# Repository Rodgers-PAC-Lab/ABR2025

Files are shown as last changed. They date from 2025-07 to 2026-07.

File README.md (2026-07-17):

# ABR2025

## Introduction

This repository contains code to implement the ABR measuring system described
in Gargiullo et al, as well as the analysis scripts needed to replicate the 
figures in that paper.
Preprint: https://www.biorxiv.org/content/10.64898/2025.12.17.694771v1

The repository is structured as follows:
- `./` - The toplevel directory, containing this README file
- `./designs` - Design files, bill of materials, and other information about 
physically building the system.
- `./src` - source code for analysis and GUI. Import like `import opensabr`
- `./src/gui` - A Python module for running the graphical user interface (GUI) 
to take ABR data. It can be imported like `import opensabr.gui`. This code is 
run on a desktop PC connected to the ABR measuring system hardware.
- `./scripts` - A folder of demo scripts that generate the figures in the
paper, using data that we collected and have shared on Zenodo. These scripts 
are meant to be run one at a time, not imported and called by other scripts. 

## Requirements

We used Python 3.11. Newer versions may also work but we did not test them.

requirements-lock.txt includes the exact versions we used

For the analysis scripts (but not the GUI), the following repository is 
required. It should be on your PYTHONPATH so that it can be imported using
the syntax `import my`.
- `git clone git@github.com:Rodgers-PAC-Lab/my.git`

TODO: only my.plot is needed, bring minimal into this repo

## Instructions

To build the hardware, refer to the file `./designs/README`. 

To run the GUI and measure ABR, refer to the file `./gui/README`.

To run the analysis scripts and regenerate the figures included in the paper,
refer to the file `./scripts/README`.

## Overall installation instructions
These instructions walk you through the installation of OpenSABR, our fork
of ABRA, and our fork of ABRpresto in three different conda environments.
If you only want to run OpenSABR, you can skip the other two environments --
they are only used to provide a point of comparison in the paper. 

We clone repositories that are installed using a method like `pip install`
into a directory called `~/dev/installed`. We clone repositories that are 
not installable, but need to be imported, into a directory called `~/dev`.
ABRA is the only one that must be cloned into `~/dev`.
This is because it can cause errors to mix these two kinds of repositories.
`~/dev` must be on the PYTHONPATH for this to work. 

For ABRA, we recommend the CPU packages, there is no need for GPU.

The three conda environments share data written to disk in the parquet format.

## Installing OpenSABR
# Clone repo
cd ~/installed
git clone git@github.com:Rodgers-PAC-Lab/OpenSABR
cd OpenSABR

# --- Install: pick ONE of Option A or Option B ---

# Option A: Typical install (no version pins)
conda create -n opensabr -c conda-forge python=3.11 pip ipython
conda activate opensabr
conda install -c conda-forge numpy scipy pandas matplotlib tqdm pyqt pyqtgraph pyserial pyarrow seaborn
pip install -e . --no-deps

# Option B: Reproducible install from lock (linux-64 only)
conda create -n opensabr --file opensabr-conda-lock.txt
conda activate opensabr
pip install -e . --no-deps

## Installing ABRpresto
# Clone repo
cd ~/installed 
git clone git@github.com:Rodgers-PAC-Lab/ABRpresto # our fork
cd ABRpresto
git checkout dev # our branch with fixes

# --- Install: pick ONE of Option A or Option B ---

# Option A: Typical install (no version pins)
conda create -n abrpresto -c conda-forge python=3.11 ipython pip
conda activate abrpresto
conda install -c conda-forge numpy scipy pandas matplotlib setuptools_scm pyarrow tqdm
pip install -e . --no-deps

# Option B: Reproducible install from lock (linux-64 only)
conda create -n abrpresto --file abrpresto-conda-lock.txt
conda activate abrpresto
pip install -e . --no-deps

## Installing ABRA
# Clone repo (must be under ~/dev or some location on PYTHONPATH)
cd ~/dev
git clone git@github.com:Rodgers-PAC-Lab/abranalysis # our fork
cd abranalysis
git checkout dev # our branch with fixes

# --- Install: pick ONE of Option A or Option B ---
# ABRA cannot be pip-installed; it is imported via PYTHONPATH in both options.

# Option A: Typical install (no version pins)
conda create -n abra -c conda-forge python=3.11 ipython pip
conda activate abra
conda install -c conda-forge numpy scipy pandas scikit-learn pytorch=*=cpu* keras tensorflow streamlit easydict "altair<5" pyarrow matplotlib tqdm
conda env config vars set PYTHONPATH=$HOME/dev
conda deactivate && conda activate abra   # reload so PYTHONPATH takes effect

# Option B: Reproducible install from lock (linux-64 only)
conda create -n abra --file abra-conda-lock.txt
conda activate abra
conda env config vars set PYTHONPATH=$HOME/dev
conda deactivate && conda activate abra   # reload so PYTHONPATH takes effect

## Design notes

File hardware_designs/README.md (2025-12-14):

# ABR2025 - hardware designs

## Introduction 

This folder contains the designs needed to build the hardware for the 
ABR measuring system described in Gargiullo 2025.

It contains the following subfolders:
- bill_of_materials.xlsx: Bill of Materials for all required parts
- interface_pcb/: PCB design files for the "interface PCB" that houses the
Teensy and connects to the other boards
- teensy/: Files for the code that runs on the Teensy

### Bill of Materials

This is an Excel file of all required components. You will also need standard
electronics equipment for soldering, etc.

### Interface PCB

This PCB was designed in Eagle. The original design files are located in the
`eagle` subdirectory and can be opened in the Eagle software. You only need to 
do this if you want to edit the PCB.

If you just want to print the PCB, use the files in the `gerbers` subdirectory.
These are the standard manufacturing format that all PCB printing companies use.
We used OSH Park to print the PCB.

After you receive the PCB, you will need to populate a few components. Details
are available in the "Supplemental Material", which also explains how to 
physically assemble all components.

### Teensy files

This is the software that runs on the Teensy. The software controls the 
ADS1299, and it also interfaces with the desktop computer running the GUI
(see `../gui/README`). Flash the files included here on the Teensy.

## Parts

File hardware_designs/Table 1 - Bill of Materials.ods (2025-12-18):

Item # | Component name | Manufacturer | Part number | Vendor | Quantity | Price per unit | Total price | Notes | Link
1 | ADS1299 Performance Demonstration Kit | TI | ADS1299EEGFE-PDK | Ti | 1 | 199 | 199 | Available on Digikey for $238. Added to the DigiKey BOM but don't recoomend buying through them due to markup. | https://www.ti.com/tool/ADS1299EEGFE-PDK
2 | Teensy 4.0 | Sparkfun | 1568-15583-ND | DigiKey | 1 | 23.8 | 23.8 |  | https://www.digikey.com/en/products/detail/sparkfun-electronics/15583/10384551
3 | Mini banana plug solderless stacking | Pomona | 2945 | DigiKey | 9 | 6.09 | 54.81 | 2 each * 4 channels (3 neural channels + audio channel) + 1 for ground. On DigiKey list version of this BOM I added red and black versions. | https://www.digikey.com/en/products/base-product/pomona-electronics/501/2945/525904
4 | Mini banana jack (turret style) | Pomona | 2142-2 | DigiKey | 9 | 2.9 | 26.1 | On DigiKey list version of this BOM I added red and black versions. | https://www.digikey.com/en/products/base-product/pomona-electronics/501/2142/427743
5 | Mini grabber solder 0.090" | Pomona | 3925 | DigiKey | 6 | 2.54 | 15.24 | 3 for electrodes, 1 for ground electrode, 2 for speaker power. On DigiKey list version of this BOM I added grabbers of several different colors | https://www.digikey.com/en/products/base-product/pomona-electronics/501/3925/525917
6 | USB-B to USB-A adapter | Switchcraft Inc | SC1837-ND | DigiKey | 1 | 22.26 | 22.26 | USB form factor not important, just needs a panel mount feed-through | https://www.digikey.com/en/products/detail/switchcraft-inc/EHUSBBABX/1832371
7 | 3/4" #4-40 Aluminum hex standoff | Keystone Electronics | 36-8403-ND | DigiKey | 4 | 0.71 | 2.84 | Supports interface PCB, 2x stacked on 2 legs | https://www.digikey.com/en/products/detail/keystone-electronics/8403/255370
8 | 7/8" #4-40 Aluminum hex standoff | Keystone Electronics | 36-8404-ND | DigiKey | 2 | 1 | 2 | Supports ADS1299 daughterboard | https://www.digikey.com/en/products/detail/keystone-electronics/8404/255371
9 | 3/8" #4-40 nylon hex standoff F-F | Keystone Electronics | 36-1902B-ND | DigiKey | 4 | 0.62 | 2.48 | Glued to bottom of MMB0 | https://www.digikey.com/en/products/detail/keystone-electronics/1902B/61866
10 | Hammond 1598GBK | Hammond | 1598 GBK | DigiKey | 1 | 27.86 | 27.86 | Device enclosure | https://www.digikey.com/en/products/detail/hammond-manufacturing/1598GBK/131059
11 | DC-to-DC converter | Recom power | R-78E5.0-0.5 | DigiKey | 1 | 3.3 | 3.3 | Step-down 9V to Teensy | https://www.digikey.com/en/products/detail/recom-power/R-78E5-0-0-5/2834904
12 | 3-conductor cable (24 AWG) | Tensility | 30-01424 | DigiKey | 1 | 5.17 | 5.17 | Priced per meter | https://www.digikey.com/en/products/detail/tensility-international-corp/30-01424/13151644
13 | Molex KK254 2-pin PCB header | Molex | 900-002222021-ND | DigiKey | 1 | 0.16 | 0.16 | Power connector X1 on interface PCB | https://www.digikey.com/en/products/detail/molex/0022232021/26667
14 | Molex KK254 2-pos receptacle | Molex | 900-0022013027-ND | DigiKey | 1 | 0.1 | 0.1 | Power cable connector for MMB0 power to interface PCB | https://www.digikey.com/en/products/detail/molex/0022013027/26431
15 | Pre-crimped 12" A2016 (KK254 series) wires | Molex | 0008500113-12-B2-D-ND | DigiKey | 2 | 0.85 | 1.7 | Fits into KK254 power cable receptacle | https://www.digikey.com/en/products/detail/molex/0008500113-12-B2-D/5991033
16 | 10 µH Inductor | Taiyo Yuden | 587-1625-1-ND | DigiKey | 2 | 0.18 | 0.36 |  | https://www.digikey.com/en/products/detail/taiyo-yuden/CBC3225T100MR/958009
17 | 220 µF capacitor | Panasonic | PCE3839CT-ND | DigiKey | 1 | 0.85 | 0.85 |  | https://www.digikey.com/en/products/detail/panasonic-electronic-components/EEE-FK1V221P/766007
18 | 100 µF capacitor | Nichicon | 493-3937-1-ND | DigiKey | 1 | 0.61 | 0.61 |  | https://www.digikey.com/en/products/detail/nichicon/UCL1E101MCL1GS/2300286
19 | 1 µF capacitor | Samsung | 1276-1066-1-ND | DigiKey | 1 | 0.08 | 0.08 |  | https://www.digikey.com/en/products/detail/samsung-electro-mechanics/CL21B105KAFNNNE/3886724
20 | 0.1 µF (100 nF) capacitor | Samsung | 1276-1099-1-ND | DigiKey | 3 | 0.08 | 0.24 |  | https://www.digikey.com/en/products/detail/samsung-electro-mechanics/CL21B104KACNNNC/3886757
21 | Needle electrodes | Rochestor Horizon | NS-S86015-R1-10 | Lifesync | 4 per recording |  |  | 4 electrodes per recording (L, R, V, GND) | https://lifesync.com/products/horizon-multilead-ribbon-subdermal-needle-electrodes-variants
22 | Speaker- horn tweeter | Fostex | FT17H | Fostex | 2 | NA | NA |  | Discontinued
23 | USB serial UART converter | Acroname | S27-USB-SERIAL | Acroname | 1 | 12.5 | 12.5 | Optional | https://acroname.com/store/s27-usb-serial#assets

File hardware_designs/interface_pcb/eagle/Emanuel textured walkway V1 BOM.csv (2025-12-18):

Partlist exported from C:/Users/Bill/Dropbox/EAGLE/projects/
Alan Emanuel textured walkway/Emanuel textured walkway V1.sch at 4/9/2025 10:39 AM
Qty | Value | Device | Parts
3 | 1uF | C-USC0805 | C5, C6, C7
1 | 3.3 | TP-040-100 | 3.3
3 | 10uH | L-USL1812 | L1, L2, L3
1 | 22-23-2021 | 22-23-2021 | X1
1 | 74LS14D | 74LS14D | IC10
2 | 78E-5V | RECOM-R-78E | IC8, IC9
1 | 78E-12V | RECOM-R-78E | IC7
3 | 100/35 | CPOL-US140CLH-0810 | C2, C3, C4
3 | 100nF | C-USC0805 | C8, C9, C10
1 | 330/35 | CPOL-US140CLH-1010 | C1
6 | BTS3118N | BTS3118N | IC1, IC2, IC3, IC4, IC5, IC6
1 | EXTRA | ML16 | SV3
1 | I/O-1 | ML16 | SV2
1 | STEPPER | ML16 | SV1
1 | TEENSY_4.0_WITH_24-33 | TEENSY_4.0_WITH_24-33 | U$1
38 | TP-040-100 | TP-040-100 | +5B, 6, 7, 22, 23, 24, 25, 26, 27, 28, 29, 30, 31, 32, 33, E9, E10, E11, E12, E13, E14, E15, E16, EI1, EI2, EI3, EO1, EO2, EO3, MISO, MOSI, RX1, SCK, TX1, VI3, VS1, VS2, VS3
1 | TRCV-175-LARGE | TRCV-175-LARGE | J1

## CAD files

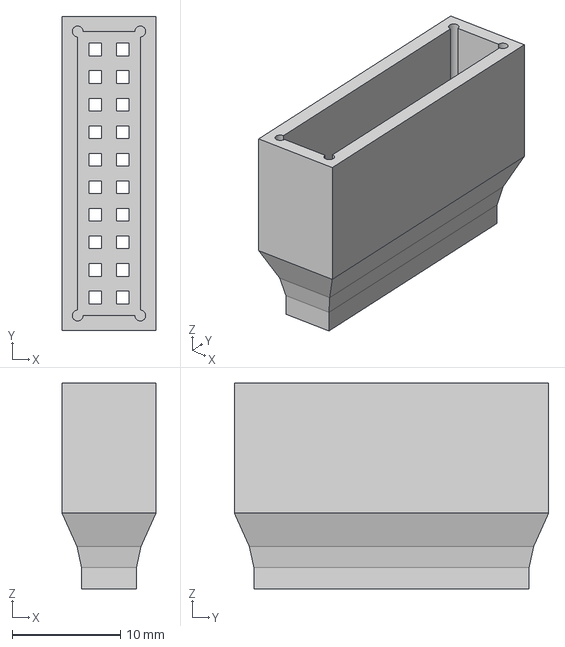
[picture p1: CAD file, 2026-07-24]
hardware_designs/3D_print_designs/2x10 male pin header spacer.step
8.68 x 29.0 x 19.0 mm

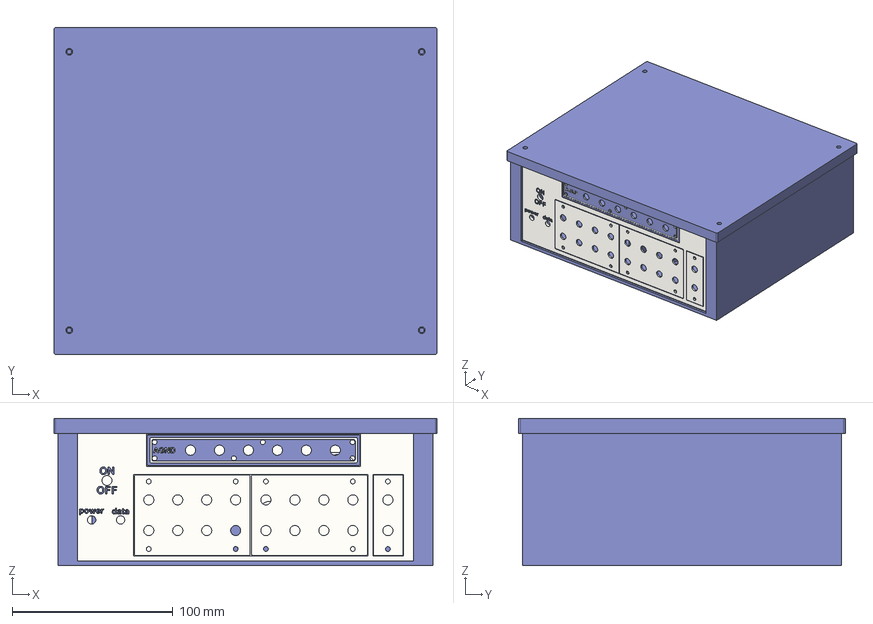
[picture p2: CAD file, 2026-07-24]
hardware_designs/3D_print_designs/Compact ABR enclosure.step
238.0 x 203.0 x 91.5 mm
face plate
Back plate
Lid

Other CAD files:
hardware_designs/3D_print_designs/2x10 male pin header spacer.3mf
hardware_designs/3D_print_designs/2x10 male pin header spacer.f3d
hardware_designs/3D_print_designs/Compact ABR enclosure.3mf
hardware_designs/3D_print_designs/Compact ABR enclosure.f3z

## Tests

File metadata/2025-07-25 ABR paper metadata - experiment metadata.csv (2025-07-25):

date | experimenter | mouse
2025-04-30 | rowan | Pearl_189
2025-05-02 | rowan | Cacti_1
2025-05-06 | rowan | Cat_226
2025-05-06 | rowan | Cat_227
2025-05-09 | rowan | Cat_226
2025-05-09 | rowan | Cat_227
2025-05-12 | rowan | Cat_226
2025-05-12 | rowan | Cat_227
2025-05-14 | rowan | Cat_226
2025-05-14 | rowan | Cat_227
2025-05-15 | rowan | Cat_228
2025-05-15 | rowan | Cat_229
2025-05-20 | rowan | Cat_228
2025-05-20 | rowan | Cat_229
2025-05-24 | rowan | Cat_228
2025-05-24 | rowan | Cat_229
2025-05-27 | rowan | Cat_228
2025-05-27 | rowan | Cat_229
2025-06-02 | rowan | Cacti_223
2025-06-02 | rowan | Cacti_225
2025-06-06 | rowan | Cacti_223
2025-06-06 | rowan | Cacti_224

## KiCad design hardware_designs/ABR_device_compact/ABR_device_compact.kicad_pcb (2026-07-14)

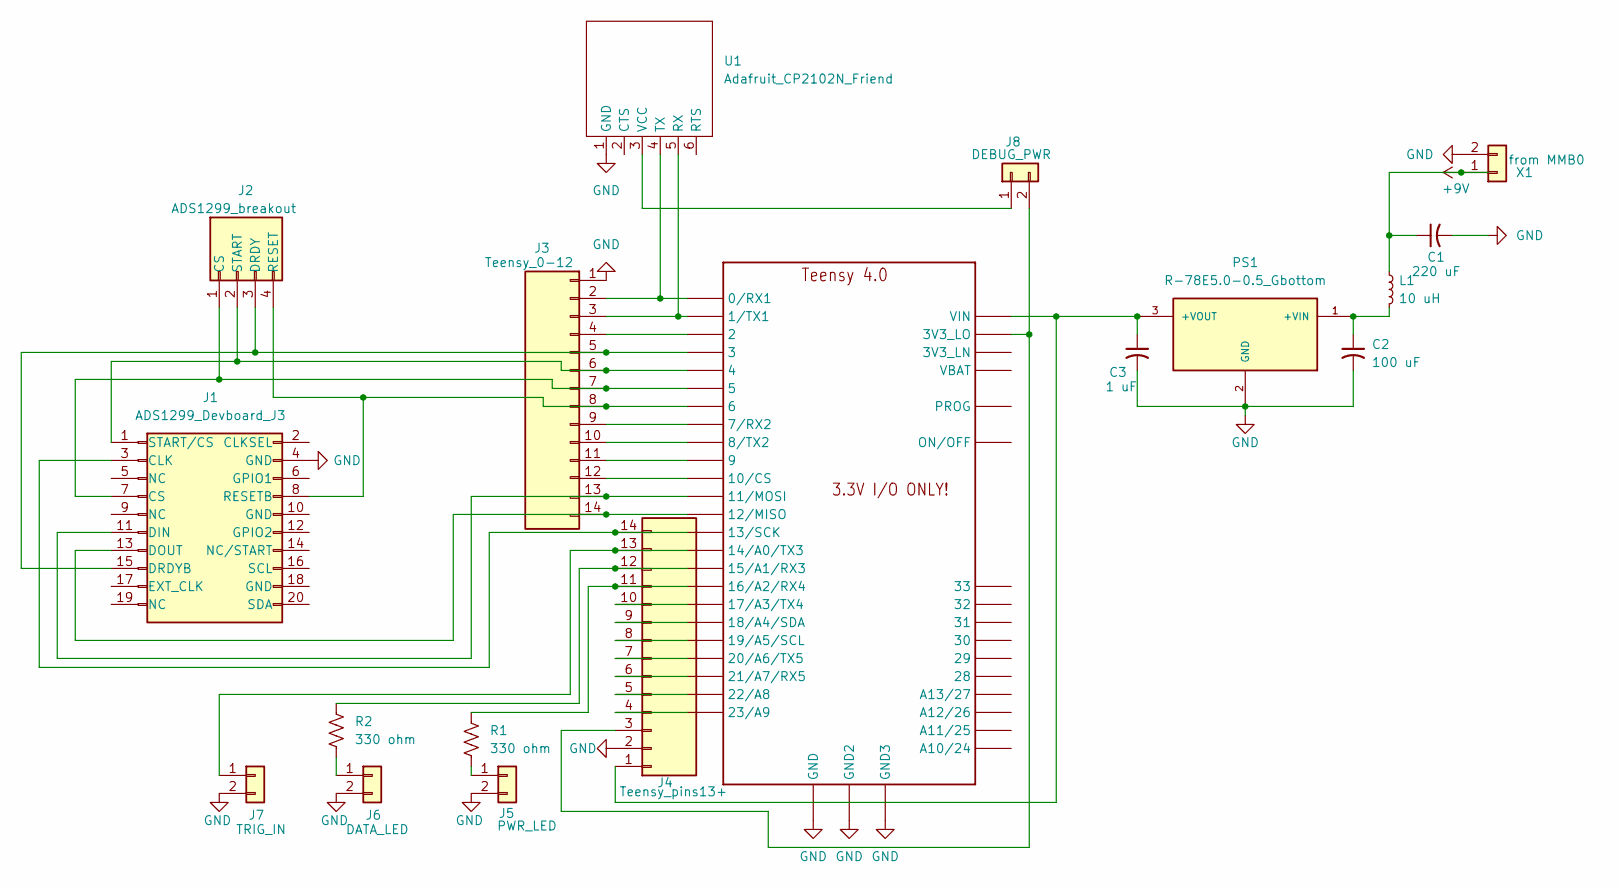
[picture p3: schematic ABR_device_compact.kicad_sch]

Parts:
1: TEENSY_4.0_WITH_24-33
C1: 220 uF; CP_Radial_D10.0mm_P5.00mm
C2: 100 uF; CP_Radial_D8.0mm_P3.80mm
C3: 1 uF; CP_Radial_D7.5mm_P2.50mm
J1: ADS1299_Devboard_J3; IDC-Header_2x10_P2.54mm_Vertical
J2: ADS1299_breakout; PinSocket_1x04_P2.54mm_Vertical
J3: Teensy_0-12; PinHeader_1x14_P2.54mm_Vertical
J4: Teensy_pins13+; PinHeader_1x14_P2.54mm_Vertical
J5: PWR_LED; PinHeader_1x02_P2.54mm_Vertical
J6: DATA_LED; PinHeader_1x02_P2.54mm_Vertical
J7: TRIG_IN; PinHeader_1x02_P2.54mm_Vertical
J8: DEBUG_PWR; PinHeader_1x02_P2.54mm_Vertical
L1: 10 uH; L_Axial_L9.5mm_D4.0mm_P15.24mm_Horizontal_Fastron_SMCC
PS1: R-78E5.0-0.5_Gbottom; CONV_R-78E5.0-0.5; PARTREV v4
R1, R2: 330 ohm; R_Axial_DIN0207_L6.3mm_D2.5mm_P10.16mm_Horizontal
U1: Adafruit_CP2102N_Friend
X1: from MMB0; JST_XH_B2B-XH-A_1x02_P2.50mm_Vertical

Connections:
+9V: C1.1, L1.1, X1.1
GND: 1.GND, 1.GND2, 1.GND3, C1.2, C2.2, C3.2, J1.4 (GND), J3.1, J4.2, J5.2, J6.2, J7.2, PS1.2 (GND), U1.1 (GND), X1.2
unnamed: 1.0/RX (0/RX1), J3.2, U1.4 (TX)
unnamed: 1.1/TX (1/TX1), J3.3, U1.5 (RX)
unnamed: 1.7 (7/RX2), J3.9
unnamed: 1.8 (8/TX2), J3.10
unnamed: 1.14/A0 (14/A0/TX3), J4.13, J7.1
unnamed: 1.15/A1 (15/A1/RX3), J4.12, R2.1
unnamed: 1.16/A2 (16/A2/RX4), J4.11, R1.1
unnamed: 1.17/A3 (17/A3/TX4), J4.10
unnamed: 1.20/A6 (20/A6/TX5), J4.7
unnamed: 1.21/A7 (21/A7/RX5), J4.6
unnamed: 1.13/SCK, J1.3 (CLK), J4.14
unnamed: 1.5, J1.7 (CS), J2.1 (CS), J3.7
unnamed: 1.11/MOSI, J1.11 (DIN), J3.13
unnamed: 1.12/MISO, J1.13 (DOUT), J3.14
unnamed: 1.3, J1.15 (DRDYB), J2.3 (DRDY), J3.5
unnamed: 1.6, J1.8 (RESETB), J2.4 (RESET), J3.8
unnamed: 1.4, J1.1 (START/CS), J2.2 (START), J3.6
unnamed: 1.2, J3.4
unnamed: 1.9, J3.11
unnamed: 1.10/CS, J3.12
unnamed: 1.VIN, C3.1, J4.1, PS1.3 (+VOUT)
unnamed: 1.3V3_LO, J4.3, J8.2
unnamed: 1.23/A9, J4.4
unnamed: 1.22/A8, J4.5
unnamed: 1.19/A5/SCL, J4.8
unnamed: 1.18/A4/SDA, J4.9
unnamed: J5.1, R1.2
unnamed: J6.1, R2.2
unnamed: J8.1, U1.3 (VCC)
unnamed: C2.1, L1.2, PS1.1 (+VIN)

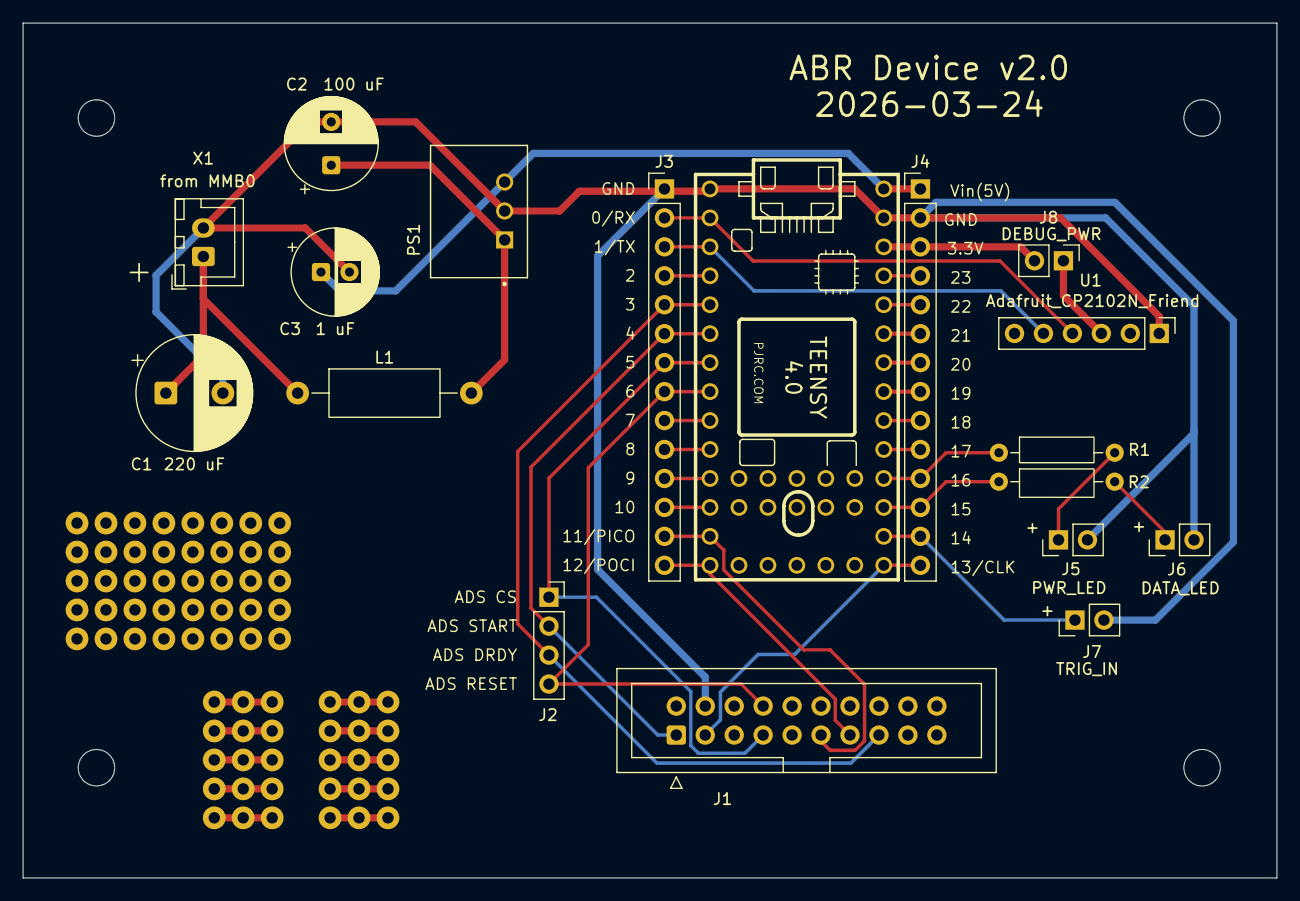
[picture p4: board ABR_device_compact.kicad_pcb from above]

Board: 2 copper layers, 110.0 x 75.0 mm, 87 parts (0 on the bottom side), 32 nets.

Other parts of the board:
2, 3, 4, 5, 6, 7, 8, 9, 9#2, 10, 11, 12, 13, 14, 15, 16, 17, 17#2, 18, 19, 20, 21, 22, 23, 24, 25, 25#2, 26, 27, 28, 29, 30, 31, 32, 33, 34, 35, 36, 37, 38, 39, 40, 41, 41#2, 42, 43, 44, 45, 46, 47, 48, 49, 57, 58, 59, 60, 61, 62, 63, 64, 65, 66, 67, 68, 69, 70, 71, 72, 73: (no value)

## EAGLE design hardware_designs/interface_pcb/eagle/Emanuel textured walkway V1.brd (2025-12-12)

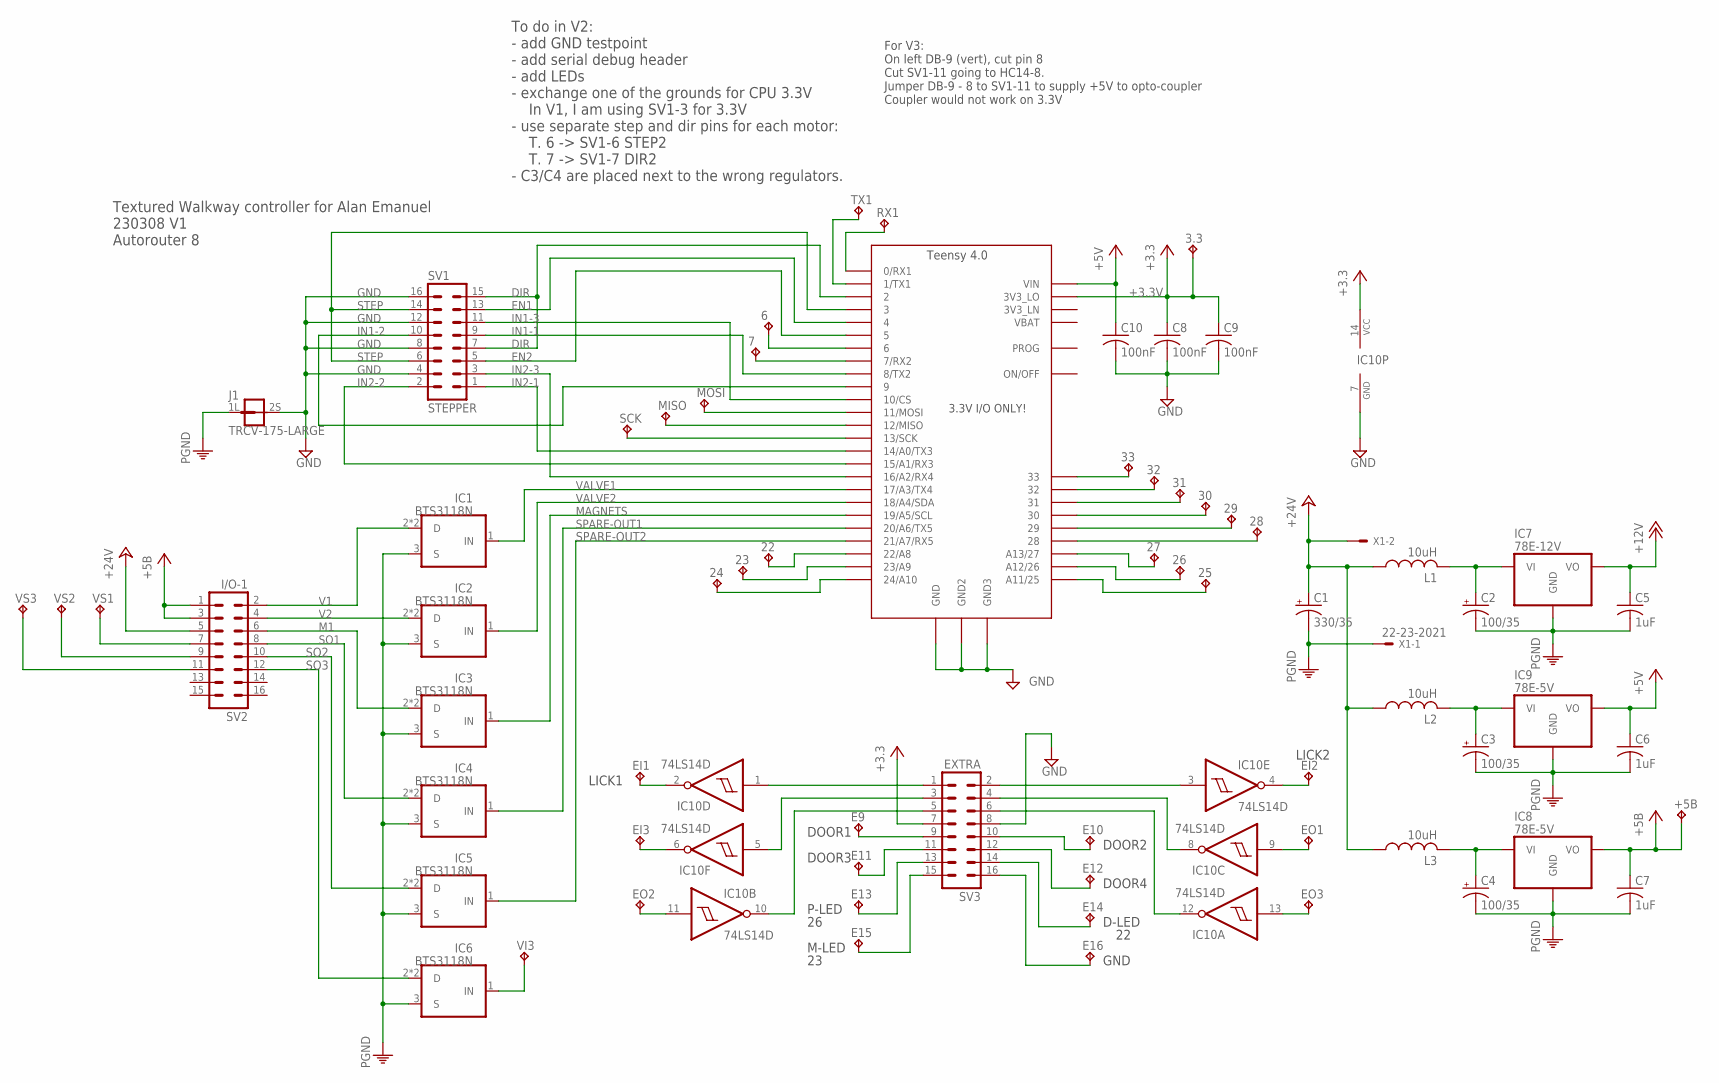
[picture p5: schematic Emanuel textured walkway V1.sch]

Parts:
3.3: 3.3; P1-040-100
6, 7, 22, 23, 24, 25, 26, 27, 28, 29, 30, 31, 32, 33: TP-040-100; P1-040-100
+5B: TP-040-100; P1-040-100
C1: 330/35; 140CLH-1010
C2, C3, C4: 100/35; 140CLH-0810
C5, C6, C7: 1uF; C0805
C8, C9, C10: 100nF; C0805
E9, E10, E11, E12, E13, E14, E15, E16: TP-040-100; P1-040-100
EI1, EI2, EI3: TP-040-100; P1-040-100
EO1, EO2, EO3: TP-040-100; P1-040-100
IC1, IC2, IC3, IC4, IC5, IC6: BTS3118N; SOT223
IC7: 78E-12V; RECOM-R-78E
IC8, IC9: 78E-5V; RECOM-R-78E
IC10: 74LS14D; SO14
J1: TRCV-175-LARGE; JUMPER-TRACE-CONVERT-LARGER-PADS-175
L1, L2, L3: 10uH; L1812
MISO: TP-040-100; P1-040-100
MOSI: TP-040-100; P1-040-100
RX1: TP-040-100; P1-040-100
SCK: TP-040-100; P1-040-100
SV1: STEPPER; ML16
SV2: I/O-1; ML16
SV3: EXTRA; ML16
TX1: TP-040-100; P1-040-100
U$1: TEENSY_4.0_WITH_24-33
VI3: TP-040-100; P1-040-100
VS1, VS2, VS3: TP-040-100; P1-040-100
X1: 22-23-2021

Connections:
+3.3V: 3.3.P$1, C8.1, C9.1, IC10.14 (VCC), SV3.7, U$1.3V3_LO
+5B: +5B.P$1, C7.1, IC8.3 (VO), SV2.1, SV2.3
+5V: C6.1, C10.1, IC9.3 (VO), U$1.VIN
+12V: C5.1, IC7.3 (VO)
+24V: C1.+, L1.1, L2.1, L3.1, SV2.5, X1.2
DIR: SV1.7, SV1.15, U$1.2
EN1: SV1.13, U$1.4
EN2: SV1.5, U$1.5
GND: C8.2, C9.2, C10.2, IC10.7 (GND), J1.2S (2), SV1.4, SV1.8, SV1.12, SV1.16, SV3.8, U$1.GND, U$1.GND2, U$1.GND3
IN1-1: SV1.9, U$1.8 (8/TX2)
IN1-2: SV1.10, U$1.9
IN1-3: SV1.11, U$1.10/CS
IN2-1: SV1.1, U$1.14/A0 (14/A0/TX3)
IN2-2: SV1.2, U$1.15/A1 (15/A1/RX3)
IN2-3: SV1.3, U$1.16/A2 (16/A2/RX4)
M1: IC3.2 (D), IC3.4 (D), SV2.6
MAGNETS: IC3.1 (IN), U$1.19/A5/SCL
unnamed: C2.+, IC7.1 (VI), L1.2
unnamed: C4.+, IC8.1 (VI), L3.2
unnamed: SV2.9, VS2.P$1
unnamed: SV2.11, VS3.P$1
unnamed: C3.+, IC9.1 (VI), L2.2
unnamed: IC6.1 (IN), VI3.P$1
unnamed: MOSI.P$1, U$1.11/MOSI
unnamed: MISO.P$1, U$1.12/MISO
unnamed: SV2.7, VS1.P$1
unnamed: SCK.P$1, U$1.13/SCK
unnamed: 22.P$1, U$1.22/A8
unnamed: 23.P$1, U$1.23/A9
unnamed: 24.P$1, U$1.24 (24/A10)
unnamed: 33.P$1, U$1.33
unnamed: 32.P$1, U$1.32
unnamed: 31.P$1, U$1.31
unnamed: 30.P$1, U$1.30
unnamed: 29.P$1, U$1.29
unnamed: 28.P$1, U$1.28
unnamed: 27.P$1, U$1.27 (A13/27)
unnamed: 26.P$1, U$1.26 (A12/26)
unnamed: 25.P$1, U$1.25 (A11/25)
unnamed: RX1.P$1, U$1.0/RX (0/RX1)
unnamed: TX1.P$1, U$1.1/TX (1/TX1)
unnamed: 6.P$1, U$1.6
unnamed: 7.P$1, U$1.7 (7/RX2)
unnamed: IC10.1 (I), SV3.1
unnamed: IC10.3 (I), SV3.2
unnamed: IC10.5 (I), SV3.3
unnamed: IC10.8 (O), SV3.4
unnamed: IC10.10 (O), SV3.5
unnamed: IC10.12 (O), SV3.6
unnamed: E9.P$1, SV3.9
unnamed: E11.P$1, SV3.11
unnamed: E13.P$1, SV3.13
unnamed: E15.P$1, SV3.15
unnamed: E10.P$1, SV3.10
unnamed: E12.P$1, SV3.12
unnamed: E14.P$1, SV3.14
unnamed: E16.P$1, SV3.16
unnamed: EI1.P$1, IC10.2 (O)
unnamed: EI3.P$1, IC10.6 (O)
unnamed: EI2.P$1, IC10.4 (O)
unnamed: EO3.P$1, IC10.13 (I)
unnamed: EO1.P$1, IC10.9 (I)
unnamed: EO2.P$1, IC10.11 (I)
PGND: C1.-, C2.-, C3.-, C4.-, C5.2, C6.2, C7.2, IC1.3 (S), IC2.3 (S), IC3.3 (S), IC4.3 (S), IC5.3 (S), IC6.3 (S), IC7.2 (GND), IC8.2 (GND), IC9.2 (GND), J1.1L (1), X1.1
SO1: IC4.2 (D), IC4.4 (D), SV2.8
SO2: IC5.2 (D), IC5.4 (D), SV2.10
SO3: IC6.2 (D), IC6.4 (D), SV2.12
SPARE-OUT1: IC4.1 (IN), U$1.20/A6 (20/A6/TX5)
SPARE-OUT2: IC5.1 (IN), U$1.21/A7 (21/A7/RX5)
STEP: SV1.6, SV1.14, U$1.3
V1: IC1.2 (D), IC1.4 (D), SV2.2
V2: IC2.2 (D), IC2.4 (D), SV2.4
VALVE1: IC1.1 (IN), U$1.17/A3 (17/A3/TX4)
VALVE2: IC2.1 (IN), U$1.18/A4/SDA

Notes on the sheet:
Textured Walkway controller for Alan Emanuel 230308 V1 Autorouter 8
To do in V2: - add GND testpoint - add serial debug header - add LEDs - exchange one of the grounds for CPU 3.3V In V1, I am using SV1-3 for 3.3V - use separate step and dir pins for each motor: T. 6 -> SV1-6 STEP2 T. 7 -> SV1-7 DIR2 - C3/C4 are placed next to the wrong regulators.
LICK1
LICK2
DOOR1
DOOR3
DOOR2
DOOR4
P-LED
M-LED
D-LED
GND
For V3: On left DB-9 (vert), cut pin 8 Cut SV1-11 going to HC14-8. Jumper DB-9 - 8 to SV1-11 to supply +5V to opto-coupler Coupler would not work on 3.3V

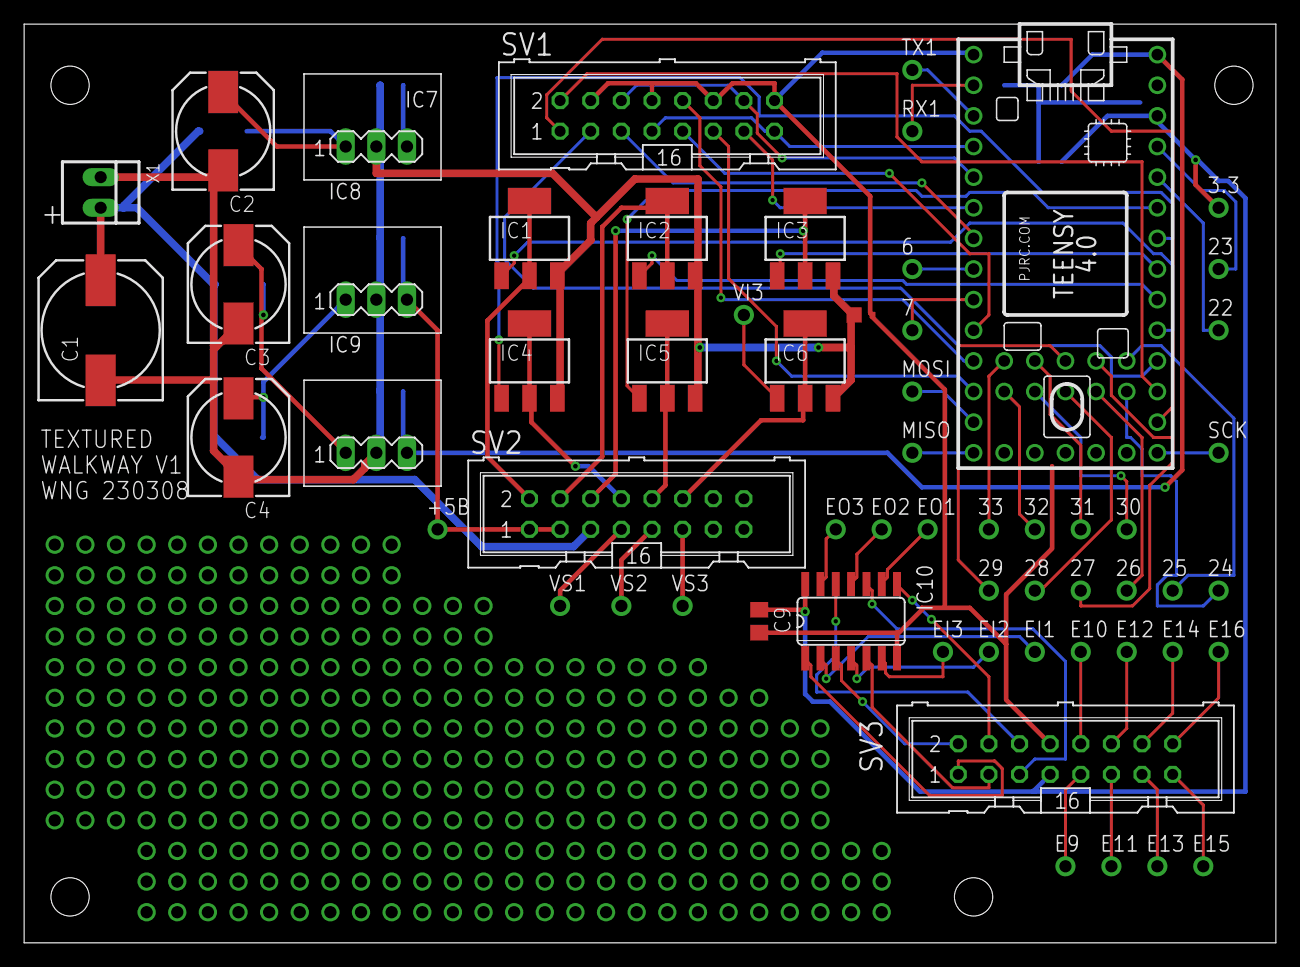
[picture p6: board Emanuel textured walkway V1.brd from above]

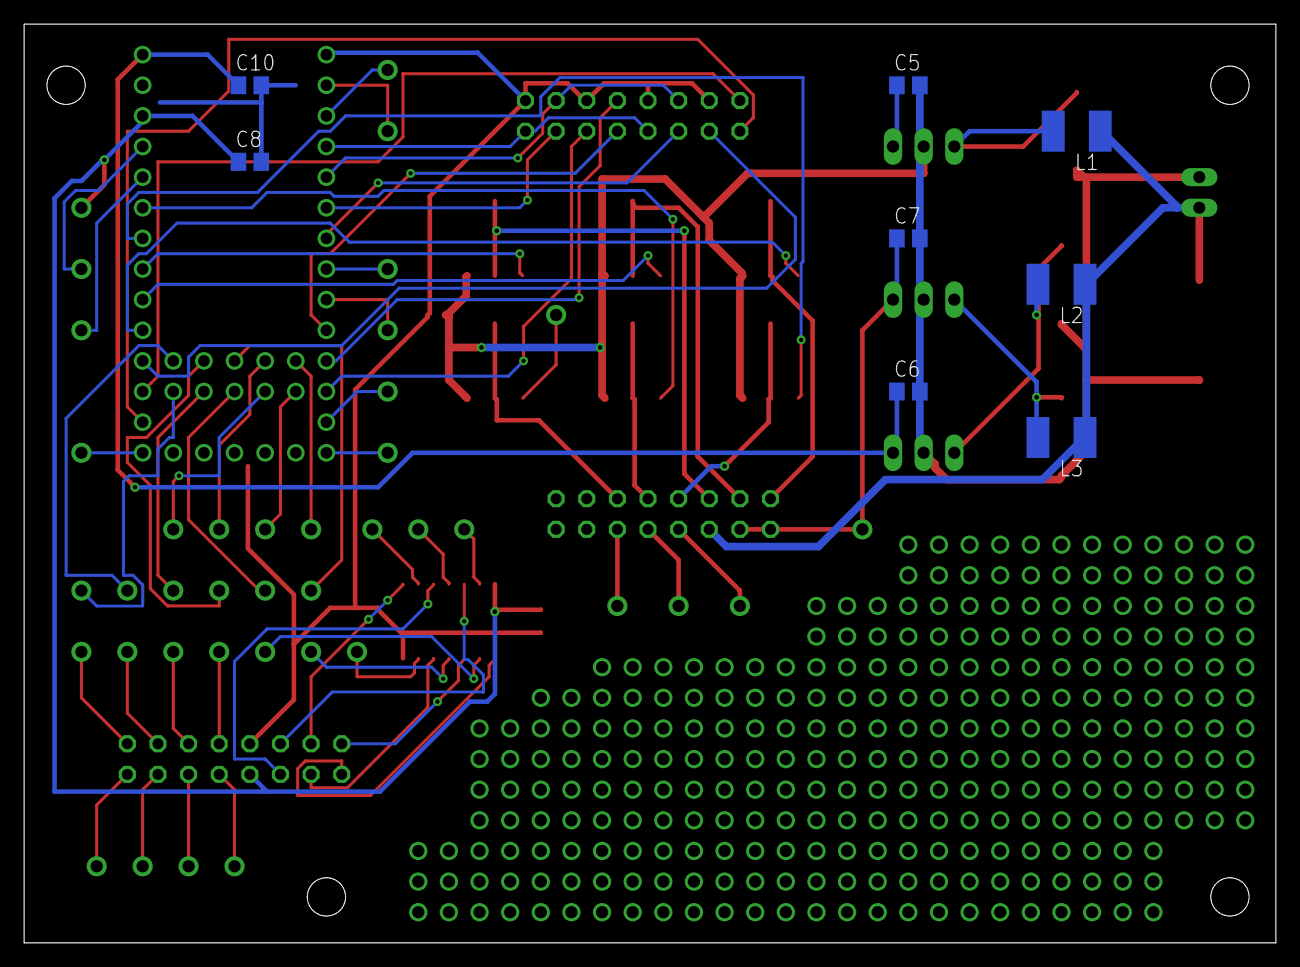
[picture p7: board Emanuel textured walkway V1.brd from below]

Board: 2 copper layers, 103.8 x 76.2 mm, 68 parts (8 on the bottom side), 74 nets.

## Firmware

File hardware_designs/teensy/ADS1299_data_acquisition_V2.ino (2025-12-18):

//                              ADS1299_data_acquisition_V2.ino

//  Bill Goolsby, Emory Cell Biology Electronics and Machining Core
//
//  Prototype for Chris Rodgers, 3/28/23.
//  Adapted from 3/10/23 version of Plessey_Human_V3.ino.
//  Uses a Textured Walkway PC board wired for the signals needed by the ADS1299
//  evaluation board.  Board has a Teensy 4.0.

//  Works with Labview program:
//  Labview\Chris Rodgers\ADS1299 data acquisition\ADS1299 data acq.llb\Test ADS1299 acquire.vi

// ***** Compilation procedure *****
// Set board to Teensy 4.0, 600MHz.  Use Arduino 2.3.2.

// Operational notes
// - If you change from one Teensy to another you must reboot the computer.
//   Just exiting and restarting Labview doesn't work.
//   This must have something to do with the changing COM port.

// Serial1 is used for debug output.

// 3/10/23 - Made some variables in loop() static.  Now works using U and S commands.
// 3/29 - removed time sync code.
// 3/31 - Data acq is working.
//   Works up to 1KHz sample rate w/ buffer size = 256, 4KHz w/ 1024, 8KHz w/ 2048,
//   16KHZ mostly w/ 3072, 16KHz w/ no visible glitches at 4000.
//   (I'm referring to ADC_BUFFER_SIZE_SAMPLES here)
//   ADS1299 board data input setup:  I disconnected the CH1 +/- input jumpers.
//   I connected (-) input to the VREFP testpoint TP3 (2.000V).  I connected (+)
//   input to the fcn. gen + output and fcn. gen GND to AGND.
//   Fcn. gen. settings: 1Vpp, zero offset, 6Hz.  
//   The signal appears in LV centered at 7.0V, max 7.5, min 6.5.
//   SPI freq = 6MHz.
//   -----
//   Changed:  delay in ISR from 10 to none, delay in sample_loop from 15 to 2,
//     removed write to g_data in ISR since this wasn't used.
//   ISR requires 43us out of 62.5us period.
//   sample_loop requires 0.5 - 1.0ms out of 31.25ms period.
// 4/10 - Added trigger input (trig_in) as interrupt on rising edge of pin 32.  
//   When triggered, the current sample number is put into LVHdrSpecs.auxSamples
//   for LV to read out.  Several changes required in LV where auxSamples was used -
//   in all those cases the value 0 is substituted.
// 4/27 - Corrected POWER_LED wiring, connected DATA_LED and toggle DATA_LED in sample_loop().
//   Added Inquire response in checkSampleLoopCommands().
// 5/04 - In ADS_ISR, changed /CS to remain low for all 27 bytes, and changed
//   sign-extend values to 0x0800000 and 0xFF000000.  Now the pk-pk range is correct
//   but there is an offset of -7.0V.  I had put -7 offset in LV Scale Data; once I
//   removed that, offset goes to zero.
// --------------------------------- V2 -------------------------------------
// 6/13 - V2.  Changes:
//   Gain is now settable per channel.  Gain array always has 8 entries.
//   U command now receives 8 gain entries.  Param array size increased to 20.
//   Trigger lockout time = 100ms.
// --------------------------------- V2B ------------------------------------
// 7/15/24 - Added impedance testing, fcn. config_impedance_test(), called from
//   setup_adc().


// To do:
// - PKT_ERROR is not being handled by LV, e.g. in S command without previous U.
// - is it necessary to copy the buffer in sample_loop?  it doesn't take much time, so don't worry about it.
// - sometimes when you stop LV, Teensy does not get the X command
// - change trig_in lockout to 50ms



#include <SPI.h>
//#include <MemoryFree.h>

#include "math.h" // for Pi and sin()

#include "src\LVDataHeader_V3\LVDataHeader_V3.h"



const String ProgName = "ADS1299 V2B";
const String dateStr  = "240719";

// *************************** TEXTURED WALKWAY V1 BOARD ****************************

//ADS1299 Teensy control lines
const int ADS_CS     =    33;  //neg true
const int ADS_RESET  =    24;  //neg true
const int ADS_START  =    25;  //pos true
const int ADS_DRDY   =    26;  //Falling transition signals data ready

const int DB0        =    27;  //debug output for ISR
const int DB1        =    28;  //debug output for sample_loop()
const int DATA_LED   =    29;  //active high
// reserve const int SPKR_IN    =    30;  //trigger input, normally low
const int POWER_LED  =    31;  //active high
const int TRIG_IN    =    32;  //trigger input, normally low

// Connections to EXTRA IDC16 on PC board
//	Fcn		Teen.	IDC16
//	SCK				 9
//	MOSI			10
//	MISO			11
//	CS		33		12
//	RESET	24		13
//	START	25		14
//	DRDY	26		15
//	GND				 8
//	TRIG_IN	32		 3  //goes through HC14 Schmidt trigger inverter.


//ADS1299 software commands - datasheet p.40
const byte SDATAC = 0x11;	// stop data continuous
const byte START  = 0x08;	// start conversion
const byte STOP   = 0x0A;	// stop conversion
const byte RDATAC = 0x10;	// enable read data continuous
const byte RREG   = 0x20;	// read register; must be ORed with x xxxx start address
							// 2nd byte = #registers to read-1, 000x xxxx
const byte WREG   = 0x40;	// write register; same comments as above


// ADS1299 REGISTER ADDRESSES
const int CONFIG1 = 0x01; // p.44
const int CONFIG2 = 0x02;
const int CONFIG3 = 0x03;
const int CH1SET  = 0x05;
const int CH2SET  = 0x06;
const int CH3SET  = 0x07;
const int CH4SET  = 0x08;
const int CH5SET  = 0x09;
const int CH6SET  = 0x0A;
const int CH7SET  = 0x0B;
const int CH8SET  = 0x0C;
// Related to impedance testing
const int LOFF        = 0x04; // p.49
const int LOFF_SENSP  = 0x0F; // p.53
const int LOFF_SENSN  = 0x10; // p.54
const int LOFF_FLIP   = 0x11; // p.55

const int NCHANS = 8; // #Hardware channels in device; always acquire this many
const int BIT_DEPTH = 24;
// Register addresses for individual channels
const byte CHREGS[NCHANS] = {CH1SET, CH2SET, CH3SET, CH4SET, CH5SET, CH6SET, CH7SET, CH8SET};



// ************************ END BOARD DEFS *******************************


const uint16_t DEVICE_ID     = 1; 
const uint16_t BOARD_VERSION = 1; //PCB version

const bool SERIAL_DEBUG = true;   //This goes over Serial2 so it can coexist with USB serial
const bool LLDB         = true;   //low-level debug; can be used at low sample rates
const int  PARAM_ARRAY_SIZE = 20; //for incoming LV commands.  Increased for new U command.

const int TRIG_IN_LOCKOUT = 100; // ms to lock out until next allowable trigger

unsigned long startTime, stopTime;

enum state_t {s_idle, s_sampling, s_error};
state_t g_State = s_idle;  //must start in idle state
bool g_setup_cmd_OK = false;  // Setup (U) must be received before Start

const int DI_SIZE = 5; //size of debug info array
struct debug_info_t;
void shift_in_debug_data(bool init, debug_info_t di, debug_info_t dia[]);
void print_debug_info(int location, int j, int rb_index, debug_info_t di[]);
struct debug_info_t {
	int  j;
	int  rbi_after_fill;
	int  pkt_seq;
	int  pkt_index;
	bool last_pkt;
};

// Specs of the ADS1299 ADC
// tclk, the master clock, is 2.048MHz, 488ns period.
// This is separate from the SPI clock.
const int16_t  ADC_REF_VOLTAGE_MV  =  4500;
const int16_t  POS_FS              =  ADC_REF_VOLTAGE_MV; //mV at GAIN = 1.  Sent to LV in Q command
const int16_t  NEG_FS              = -ADC_REF_VOLTAGE_MV; //mV at GAIN = 1
const int16_t  ZERO_OFFSET         =     0; //to be subtracted from data in LV
const uint16_t ADC_BIT_DEPTH       = BIT_DEPTH;
const uint16_t ADC_MAX_CHANNELS    =     8;
const uint16_t ADC_MIN_SAMPLE_RATE =   250;
const uint16_t ADC_MAX_SAMPLE_RATE = 16000;

// Max SPI speed for ADS1299 is 20MHz; use less for testing.
// Max sampling rate = 16KHz, period = 62.5us
// Theoretical SPI rate needed = 16Ksps * 27 bytes * 8 bits/byte = 3.46Mbps
// *** Don't make this too much faster than needed.  6MHz works.
SPISettings ADSSPISetting(6000000, MSBFIRST, SPI_MODE1); //clock idles low, capture data on falling edge

union buffer_union_t {  //Allows buffer to be viewed as int32 or uint8 for Serial.write
	int32_t  i[ADC_BUFFER_SIZE_SAMPLES]; // signed 32-bit int
	uint8_t  b[ADC_BUFFER_SIZE_BYTES];   // 4*size above - bytes for transmission
};

/*** GLOBAL ADC VARIABLES FOR THE ISR - MUST BE DECLARED VOLATILE ***/
volatile bool    g_bufferReady = false;
// Buffers for the samples to send over USB
volatile buffer_union_t buffer1;
volatile buffer_union_t buffer2;
// Buffer pointers - we want these to point to int32_t, i.e. samples, not bytes
volatile int32_t *volatile frontBuffer = &buffer1.i[0];
volatile int32_t *volatile rearBuffer  = &buffer2.i[0];
// sample counter, used in ISR
static volatile uint32_t g_buffCounter = 0; // Keeps track of the samples in buffer (ISR)
// Why is this static and others aren't?
volatile uint8_t  g_adc_nchan = NCHANS; //ISR #channels to sample. set from g_as.nchan_sample
volatile int32_t  g_recv32; //ISR signed 32-bit SPI received value
volatile uint16_t g_adci;   //counter for use in ISR
volatile bool     g_isr_enable_sampling = false; //whether ISR stores data or just returns
volatile int32_t  g_data[ADC_MAX_CHANNELS]; //signed; for testing - results for all channels
// trig_in added 4/10/23
volatile bool     g_trig_in_received = false;
volatile int16_t  g_trig_in_sampleCount = 0;
volatile uint32_t g_trig_in_time = 0; // allow 1st trig immediately
/*** END GLOBAL ADC VARIABLES ***/


unsigned long g_pktCount = 0;   //counter and timer for keeping track transfer info
unsigned long g_loopct   = 0;  
unsigned long g_bufferct = 0;
unsigned long g_pkt_sets = 0;
unsigned long g_xmit_start;     //time when sample_loop starts


#ifdef __arm__
// should use uinstd.h to define sbrk but Due causes a conflict
extern "C" char* sbrk(int incr);
#else  // __ARM__
extern char *__brkval;
#endif  // __arm__

int freeMemory() {
  char top;
#ifdef __arm__
  return &top - reinterpret_cast<char*>(sbrk(0));
#elif defined(CORE_TEENSY) || (ARDUINO > 103 && ARDUINO != 151)
  return &top - __brkval;
#else  // __arm__
  return __brkval ? &top - __brkval : &top - __malloc_heap_start;
#endif  // __arm__
}


void setup(void) {
	//io_struct_t ios;
	
	setup_pins();
	// Start serial output, 12Mbit/sec no matter what over teensy USB
	Serial.begin(115200);  //USB
	delay(1500);
	Serial1.begin(57600);  //CPU Pins 0/1 to 4-pin debug header
	delay(1500);
	char cc = 'x'; 
	while ( Serial.available() ) {  //flush USB buffer
		cc = Serial.read();
	}
	if (cc == 'x') Serial1.println(); //to quiet compiler about cc
	Serial1.print(F("Program "));  Serial.println(ProgName);

	SPI.begin(); //do this before setup_adc
	//setup_adc(ios, true, gainArray); // this will be done in U command
	Serial1.println("Setup complete");
} // end setup()


void setup_pins() {
// Set pin modes for ADS1299 interface. 
	pinMode(ADS_CS,         OUTPUT);  // ADC chip select, active low
	digitalWrite(ADS_CS,    HIGH);
	pinMode(ADS_RESET,      OUTPUT);
	digitalWrite(ADS_RESET, HIGH);
	pinMode(ADS_START,      OUTPUT);
	digitalWrite(ADS_START, LOW);
	pinMode(ADS_DRDY,       INPUT_PULLUP);
	pinMode(TRIG_IN,        INPUT);

	pinMode(DB0,            OUTPUT);
	digitalWrite(DB0,       LOW);
	pinMode(DB1,            OUTPUT);
	digitalWrite(DB1,       LOW);
	pinMode(POWER_LED,      OUTPUT);
	digitalWrite(POWER_LED, HIGH); //turn on
	pinMode(DATA_LED,       OUTPUT);
	digitalWrite(DATA_LED,  LOW); //turn off
}


void cmd_write(byte cmd) {  // Write a byte to the chip
	SPI.beginTransaction(ADSSPISetting);
		digitalWrite(ADS_CS, LOW);
		SPI.transfer(cmd);
		digitalWrite(ADS_CS, HIGH);
		delayMicroseconds(10);
	SPI.endTransaction();
}


byte cmd_write_read(byte cmd) {  // Write a byte and return result
	SPI.beginTransaction(ADSSPISetting);
		digitalWrite(ADS_CS, LOW);
		byte b = SPI.transfer(cmd);
		digitalWrite(ADS_CS, HIGH);
		delayMicroseconds(10);
	SPI.endTransaction();
	return b;
}
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

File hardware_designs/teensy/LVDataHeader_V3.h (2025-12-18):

// Used by Plessey Teensy Receiver to write data packets to Labview over USB serial connection.
// 1/08/17
// *** This spec must match Google doc "Header for serial data to Labview - Plessey Teensy" ***

// 3/29/23 - Chris Rodgers, ADS1299 prototype and Teensy 4.0.
//    Radio not used; purely USB.
//    adc_specs_t field changed to "gain".
//    adc_query_specs_t pos_fs, neg_fs and zero_offset changed to int16_t.

// Plessey Acquire V2 (Heidi) - *** Set defines to choose Rodgers or Plessey Acquire
// 6/13/23
// Changed LVHdrSpecs.auxSamples field name to trig_in_sampleCount and type
//   from uint16_t to int16_t.

#include <Arduino.h>

#define LVDataHeader_V3

#define RODGERS_LAB      // either Rodgers or Plessey Acquire
#undef  PLESSEY_ACQUIRE


// Define buffer size, no longer dependent on RF packet size.
// - Let LV choose samples/loop, probably 500.  ADC_BUFFER_SIZE_SAMPLES can be
//   larger than this as long as the total bytes per transfer is less than 61440,
//   the EDF file limit for one write.  1000Hz * 24ch (w/T/H) * 2 = 48000 bytes.

// ADS1299 version        :  500*8 samples, bytes/sample = 4
// Plessey Acquire version:  500   samples, bytes/sample = 2

#ifdef RODGERS_LAB
// ADC defines for ADS1299
const int ADC_BUFFER_SIZE_SAMPLES = (500*8);	// this must be a multiple of 8 (channels)
												// so 4000 holds 8 ch. x 500 readings
const int BYTES_PER_ADC_SAMPLE    = 4; // samples are int32_t
const int ADC_BUFFER_SIZE_BYTES   = (ADC_BUFFER_SIZE_SAMPLES * BYTES_PER_ADC_SAMPLE);
#endif

#ifdef PLESSEY_ACQUIRE
// Plessey Acquire V2, Heidi
const int ADC_BUFFER_SIZE_SAMPLES = 500;
const int BYTES_PER_ADC_SAMPLE    = 2; // samples are int16_t
const int ADC_BUFFER_SIZE_BYTES   = (ADC_BUFFER_SIZE_SAMPLES * BYTES_PER_ADC_SAMPLE);
#endif



// Packet types for data and command packets.
// *** Must match LV "Comm Commands typedef.ctl" or is it "Packet types typedef.ctl".
// Max of 32 items because field is 5 bits wide in rf_data[0].
// A valid command is "((pkt_type > PKT_1ST_COMMAND) && (pkt_type < PKT_TYPE_LAST))"

// *********************************************************************************
// *** ALWAYS UPDATE THE NEXT 3 ITEMS AND LV "PACKET TYPES TYPEDEF.CTL" TOGETHER ***
// *********************************************************************************

const int DEFINED_PKT_TYPES = 25;   //one more than the last defined type in enum below

enum PKT_TYPES {PKT_NULL             =  0,
				PKT_DATA_154         =  1, PKT_DATA_154_LAST        =  2,
				PKT_DATA_154_RESEND  =  3, PKT_DATA_154_LAST_RESEND =  4,
				// 5-6 reserved for future data types
				PKT_LV_DATA       =  7,  //from receiver to LV
				PKT_1ST_COMMAND   =  8,  //first command item; previous types are data
				PKT_STREAM_START  =  9, PKT_STREAM_STOP   = 10,  PKT_MSG_ACK       = 11,
				PKT_IDLE          = 12, PKT_ERROR         = 13,  PKT_QUERY_SPECS   = 14,
				PKT_LOG_INFO      = 15, PKT_ACK_PAYLOAD   = 16,  PKT_ADC_SPECS     = 17,
				PKT_SEND_EFFECTOR = 18, PKT_READ_EFFECTOR = 19,  PKT_RECV_PRESENT  = 20,
				PKT_NOT_FOUND     = 21, PKT_SYNC_TIME     = 22,  PKT_RESEND        = 23,
				PKT_TYPE_LAST     = 24}; //move this down as we add more valid types
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

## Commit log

2025-07-22 add metadata mouse_info.csv
    [mouse_info.csv]
2025-07-22 load from filepaths and mouse_data.csv in current directory
2025-07-22 Possible solution to the whole two mouse_info.csv thing. Add cohort name to the filename and have both in there, use RUN_STEPS1-2 to do the first two steps to both cohorts. You'll want to run Step3 i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
    [250620_HL_cohort_mouse_info.csv, 250630_cohort_mouse_info.csv]
2025-07-25 new csv
    [2025-07-25 ABR paper metadata - experiment metadata.csv, 2025-07-25 ABR paper metadata - mouse metadata.csv]
2025-08-18 add metadata to subdirectory
    [2025-07-25 ABR paper metadata - experiment metadata.csv, 2025-07-25 ABR paper metadata - mouse metadata.csv, 250620_HL_cohort_mouse_info.csv, 250630_cohort_mou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]
2025-08-18 move metadata to subfolder
    [2025-07-25 ABR paper metadata - experiment metadata.csv, 2025-07-25 ABR paper metadata - mouse metadata.csv, 250620_HL_cohort_mouse_info.csv, 250630_cohort_mou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]
2025-11-23 move everything for the paper into scripts
    [2025-07-25 ABR paper metadata - experiment metadata.csv, 2025-07-25 ABR paper metadata - mouse metadata.csv, 250620_HL_cohort_mouse_info.csv, 250630_cohort_mou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]
2025-11-23 Revert "move everything for the paper into scripts"
    This reverts commit 5d96bef88c4e92456698c6ead33062e73cff930a.
    [2025-07-25 ABR paper metadata - experiment metadata.csv, 2025-07-25 ABR paper metadata - mouse metadata.csv, 250620_HL_cohort_mouse_info.csv, 250630_cohort_mou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]
2025-11-23 Reapply "move everything for the paper into scripts"
    This reverts commit 08afd14b9bcfc3f12d41770581b7fc40990b161a.
    [2025-07-25 ABR paper metadata - experiment metadata.csv, 2025-07-25 ABR paper metadata - mouse metadata.csv, 250620_HL_cohort_mouse_info.csv, 250630_cohort_mou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]
2025-11-26 update calibration
2025-12-12 PCB files
    [Emanuel textured walkway V1 BOM.csv, Emanuel textured walkway V1.brd, Emanuel textured walkway V1.drills.xln, Emanuel textured walkway V1.sch]
2025-12-14 adding teensy file
2025-12-15 moved teensy and renamed designs
    [Emanuel textured walkway V1 BOM.csv, Emanuel textured walkway V1.brd, Emanuel textured walkway V1.drills.xln, Emanuel textured walkway V1.sch]
2025-12-15 Added bill of materials
    [Table 1 - Bill of Materials.ods]
2025-12-15 Adding teensy .cpp and .h files
